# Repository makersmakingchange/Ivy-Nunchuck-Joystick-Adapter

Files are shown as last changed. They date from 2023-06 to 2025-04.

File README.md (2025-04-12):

 # Ivy Nunchuck Joystick Adapter

The Ivy Nunchuck Adapter allows a Nunchuck Controller to be used as a USB HID Mouse or USB HID Gamepad. 

Commercially available Nunchuck Controllers have a thumbstick and two buttons. The thumbstick has a range of motion approximately ±30° (~±15 mm motion) and requires about 100 grams-force to fully deflect.

The device is comprised of off-the-shelf electronics that are assembled without the need to solder into a 3D printed enclosure. The overall cost of materials for the adapter is $20 (plus $8 for component shipping). Paired with an old Nintendo Wii Nunchuck controller or a Nunchuck Controller replacement ($10-$20), this provides a cost effective solution for an input device.

The Ivy Nunchuck Adapter can be used directly as a left or right thumbstick for the Microsoft Xbox Adaptive Controller (XAC) using the left or right USB ports.

The Ivy Nunchuck Adapter is open assistive technology (OpenAT). Under the terms of the open source licenses, the device may be built, used, and improved upon by anyone.

The current version of the Ivy Nunchuck Adapter (v1.0) has been built and user tested. 

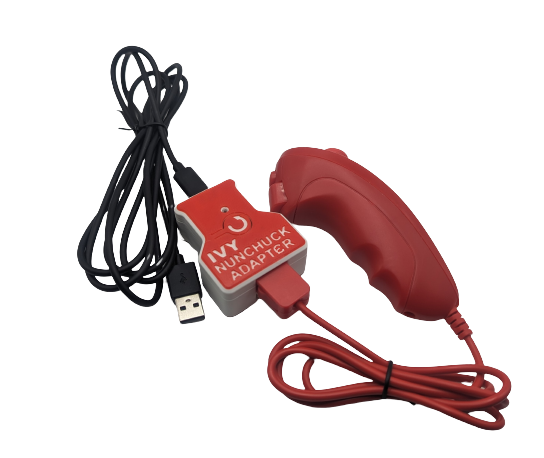
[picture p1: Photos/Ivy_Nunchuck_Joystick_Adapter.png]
An Ivy Nunchuck Adapter with a red Nunchuck controller.


MMC Assistive Device Library Listing: https://www.makersmakingchange.com/s/product/ivy-nunchuck-joystick-Adapter/01tJR0000009LBiYAM

## OpenAT Joysticks
This design is part of the [OpenAT Joystick project](https://github.com/makersmakingchange/OpenAT-Joysticks), a collection of open source designs for digital access and adapted gaming.  

## Usage
### Setup
1. Plug the Nunchuck Controller into the Ivy Nunchuck Adapter.
2. Plug the USB-C end of the USB Cable into the Ivy Nunchuck Adapter.
3. Connected the other end of the USB cable to the host device (use a suitable adapter if necessary).

### Swapping between Mouse and Gamepad Mode
1.	Reset the Adapter by pressing the Reset Button or removing and replacing the USB-C Cable.
2.	When the Status Light turns red, press and hold both the C Button and the Z Button on the Nunchuck.
3.	When the Status Light turns green, release the buttons. 
4.	Press the C button (round button) to toggle between modes. The light on the Adapter will indicate the current mode: USB HID Mouse - Yellow, USB HID Gamepad - Blue. 
5.	Press and release the Z button (square button) to set the mode. The light will blink in the colour of the selected mode.
6.	Reset the Adapter by pressing the Reset Button or removing and replacing the USB-C Cable.

### Mouse Mode
1. Move the joystick to control the cursor.
2. Press the C button to left click.
3. Press the Z button to right click.

### Gamepad Mode
1. Move the joystick to control the joystick.
2. Press the C button to activate Button 1.
3. Press the Z button to activate Button 2.

## How to Obtain a Ivy Nunchuck Adapter
There are several options for obtaining the device.

### 1. Do-it-Yourself (DIY) or Do-it-Together (DIT)

This is an open-source assistive technology, so anyone is free to build it. All of the files and instructions required to build the Ivy Nunchuck Adapter are contained within this repository. Refer to the Maker Guide below.

### 2. Request a build of this device

If you would like to obtain a Ivy Nunchuck Adapter, you may submit a build request through the [MMC Assistive Device Library Listing:](https://www.makersmakingchange.com/s/product/ivy-nunchuck-joystick-Adapter/01tJR0000009LBiYAM) to have a volunteer maker build the device. As the requestor, you are responsible for reimbursing the maker for the cost of materials and any shipping.

### 3. Build this device for someone else

If you have the skills and equipment to build this device, and would like to donate your time to create the switch for someone who needs it, visit the [MMC Maker Wanted](https://makersmakingchange.com/maker-wanted/) section.

## Build Instructions

### 1. Read through the Maker Guide
The [Maker Guide](/Documentation/Ivy_Nunchuck_Adapter_Maker_Guide.pdf) provides an overview of how to build, program, and test the device.

### 2. Use Maker Checklist
Work through the Maker Checklist. Confirm details and customization options with the user.

### 3. Order the Off-The-Shelf Components
The Bill of Materials([.csv](/Documentation/Ivy_Nunchuck_Joystick_Adapter_BOM.csv))([.xls](/Documentation/Working_Documents/Ivy_Nunchuck_Joystick_Adapter_BOM.xlsx)) lists all of the parts and components required to build the device.

### 4. Print the 3D Printable Components
Print the components for the enclosure. The print files can be found in the [/Build_Files/3D_Printing_Files](/Build_Files/3D_Printing/) folder. Reference the 3D Printing Guide section in the [Maker Guide](/Documentation/Ivy_Nunchuck_Adapter_Maker_Guide.pdf).

### 5. Assemble the Ivy Nunchuck Adapter.
Reference the Assembly Guide section of the [Maker Guide](/Documentation/Ivy_Nunchuck_Adapter_Maker_Guide.pdf) for the tools and steps required to assemble the device.

### 6. Flash the Ivy Nunchuck Adapter Firmware.
Reference the [Maker Guide](/Documentation/Ivy_Nunchuck_Adapter_Maker_Guide.pdf) for step-by-step instructions. The firmware is located in the [/Build_Files/Firmware_Files](/Build_Files/Firmware_Files/) folder.

## Files
### Documentation
| Document             | Version  | Link |
|----------------------|----------|------|
| Design Rationale     | 1.0      | [Ivy_Nunchuck_Joystick_Adapter_Design_Rationale](/Documentation/Ivy_Nunchuck_Joystick_Adapter_Design_Rationale.pdf)  |
| Maker Guide          | 1.1      | [Ivy_Nunchuck_Joystick_Adapter_Maker_Guide](/Documentation/Ivy_Nunchuck_Joystick_Adapter_Maker_Guide.pdf)          |
| Bill of Materials    | 1.0      | [Ivy_Nunchuck_Joystick_Adapter_Bill_of_Materials](/Documentation/Ivy_Nunchuck_Joystick-Adapter_BOM.csv)            |
| User Guide           | 1.0      | [Ivy_Nunchuck_Joystick_Adapter_User_Guide](/Documentation/Ivy_Nunchuck_Joystick_Adapter_User_Guide.pdf)              |

### Design Files
 - [CAD_Files](/Design_Files/CAD_Files)

### Build Files
 - [3D_Printing_Files](/Build_Files/3D_Printing_Files)
 - [Firmware_Files](/Build_Files/Firmware_Files/)

## License
Copyright (c) 2023-2025 Neil Squire / Makers Making Change.

This repository describes Open Hardware:
 - Everything needed or used to design, make, test, or prepare the Ivy Nunchuck Joystick Adapter is licensed under the [CERN 2.0 Weakly Reciprocal license (CERN-OHL-W v2) or later](https://cern.ch/cern-ohl ) .
 - All software is under the [GNU General Public License v3.0 (GPL-3.0)](https://www.gnu.org/licenses/gpl.html).
 - Accompanying material such as instruction manuals, videos, and other copyrightable works that are useful but not necessary to design, make, test, or prepare the Ivy Nunchuck Joystick Adapter are published under a [Creative Commons Attribution-ShareAlike 4.0 license (CC BY-SA 4.0)](https://creativecommons.org/licenses/by-sa/4.0/) .

You may redistribute and modify this documentation and make products using it under the terms of the [CERN-OHL-W v2](https://cern.ch/cern-ohl).
This documentation is distributed WITHOUT ANY EXPRESS OR IMPLIED WARRANTY, INCLUDING OF MERCHANTABILITY, SATISFACTORY QUALITY AND FITNESS FOR A PARTICULAR PURPOSE.
Please see the CERN-OHL-W v2 for applicable conditions.

Source Location: https://github.com/makersmakingchange/Ivy-Nunchuk-Joystick-Adapter

## Attribution
Several previous projects have interfaced with a Nunchuck controller to use it as a mouse or joystick including [USB Nunchuck Mouse](https://hackaday.io/project/188294-usbnunchuckmouse).

The [Adafruit QT Py](http://www.adafruit.com/products/4600) development board was designed by Limor Fried/Ladyada from Adafruit. The PCB design is [available open source](https://github.com/adafruit/Adafruit-QT-Py-PCB) under a CC-BY-SA license.

The [Adafruit Wii Nunchuck Breakout Adapter - Qwiic / STEMMA QT](https://www.adafruit.com/product/4836) board was designed by Limor Fried/Ladyada from Adafruit. The PCB design is [available open source](https://github.com/adafruit/Adafruit-Wii-Nunchuck-Breakout-Adapter-PCB)  under a CC-BY-SA license.

- The code utilizes the [WiiChuck](https://github.com/madhephaestus/WiiChuck) library by [Kevin Harrington (madhephaestus)](https://github.com/madhephaestus)) available under a [LGPL-3.0 license](https://www.gnu.org/licenses/lgpl-3.0.html).
 - The code also utilizes the [FlashStorage](https://github.com/cmaglie/FlashStorage) library by [Cristian Maglie (cmaglie)](https://github.com/cmaglie) available under a 
 [LGPL-2.1 license](https://www.gnu.org/licenses/lgpl-2.1.html).

 ### Contributors
- Jake McIvor, Neil Squire Society. Enclosure design, documentation, coding, testing,
- Milad Ha, Neil Squire Society. Coding.
- Josie Versloot, Neil Squire Society. Coding, testing.
- Stephen Moyer, Neil Squire Society. Testing.
- Tyler Fentie, Neil Squire Society. Testing.

---

<!-- ABOUT MMC START -->
## About Makers Making Change
[Makers Making Change Logo](https://www.makersmakingchange.com/)

Makers Making Change is a program of [Neil Squire](https://www.neilsquire.ca/), a Canadian non-profit that uses technology, knowledge, and passion to empower people with disabilities.

Makers Making Change leverages the capacity of community based Makers, Disability Professionals and Volunteers to develop and deliver affordable Open Source Assistive Technologies.

 - Website: [www.MakersMakingChange.com](https://www.makersmakingchange.com/)
 - GitHub: [makersmakingchange](https://github.com/makersmakingchange)
 - Bluesky: [@makersmakingchange.bsky.social](https://bsky.app/profile/makersmakingchange.bsky.social)
 - Instagram: [@makersmakingchange](https://www.instagram.com/makersmakingchange)
 - Facebook: [makersmakechange](https://www.facebook.com/makersmakechange)
 - LinkedIn: [Neil Squire Society](https://www.linkedin.com/company/neil-squire-society/)
 - Thingiverse: [makersmakingchange](https://www.thingiverse.com/makersmakingchange/about)
 - Printables: [MakersMakingChange](https://www.printables.com/@MakersMakingChange)

### Contact Us
For technical questions, to get involved, or to share your experience we encourage you to [visit our website](https://www.makersmakingchange.com/) or [contact us](https://www.makersmakingchange.com/s/contact).
<!-- ABOUT MMC END -->

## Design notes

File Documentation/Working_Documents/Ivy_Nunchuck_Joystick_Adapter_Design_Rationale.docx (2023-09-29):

# Introduction

The Ivy Joystick is intended to be a wearable / graspable device for those with limited gross motor control and limited hand dexterity. This design is intended to add as additional cost-effective option for people with disabilities for adapted gaming or computer access.

# Requirements

## Who

Who will be using the device?

- The device is intended for use by people with disabilities that affect their ability to use traditional input devices like computer mice and video gaming controllers, especially those with limited gross motor control and limited hand dexterity.

Who will be affected by the device?

- The primary user.

## What

What must the device do?

- Act as a USB HID Mouse and/or USB HID Gamepad.
- The device is NOT intended to be used to control a mobility device.

What needs must the device serve?

- Users with limited dexterity
- Users with the following possible points of access:
  - Hand

## Why

Why will the device be used?

- Enable / improve ability for Digital Access (e.g., control mouse function on computer)
- Enable / improve ability for Adapted Gaming (e.g., control thumbstick on Xbox Adaptive Controller)

## Where

Where will the device be used?

- In a home.
  - At a desk
  - At a wheelchair
  - On a bed
  - On a couch
- In a physical rehab setting.

## When

When will the device be used?

- When using a computer or other compatible host device (e.g., gaming console).
- When testing out different gaming set-ups.

## Goals

G01 | Achieve a material cost of less than $80 CAD.
G02 | Maker manufacturable in quantities of one.
G03 | The use of support material in 3d printed components should be minimized.
G04 | The number of different filament types should be minimized.

## Functional Requirements

| Device must be operable in USB HID Mouse operating mode
| Device must be operable in USB HID Gamepad operating mode
| Device must be compatible with the Xbox Adaptive Controller.
| Primary User should be able to switch operating mode.
| Secondary User must be able to switch operating mode
| The housing shall protect internal components from outside sources.

## Non-functional Requirement

NF01 | Device is releasable with open source license
NF02 | Device must be maker manufacturable.
NF03 | Documentation should be maintainable with the use of commonly available software.
NF04 | Documentation must be available in a digital format.
NF05 | Documentation should be printable.

## Constraints

C01 | Not for use with mobility devices.
C02 | 3D printed components shall be printable within a 180x180x180mm print volume.
C03 | 3D printed components should be printable on consumer-grade FFF printer

# Research

## Existing Commercial Options

### Wii Nunchuck

https://en.wikipedia.org/wiki/Wii

https://en.wikipedia.org/wiki/Wii_Remote

Wii Nunchuck (RVL-004)

- Analog stick
- Octagonal movement restriction
- Two trigger buttons
- Three-axis accelerometer
- 113 mm long x 38 mm wide x 37 mm thick

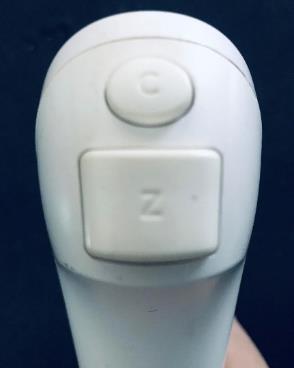
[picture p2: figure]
Nintendo Wii Nunchuk front view

Figure 1 Nintendo Wii Nunchuck. Born2BGod, CC BY-SA 4.0 <https://creativecommons.org/licenses/by-sa/4.0>, via Wikimedia Commons

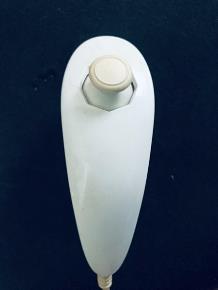
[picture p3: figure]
Nintendo Wii Nunchuk top view

Figure 2. Wii Nunchuck top. Born2BGod, CC BY-SA 4.0 <https://creativecommons.org/licenses/by-sa/4.0>, via Wikimedia Commons

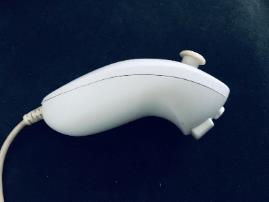
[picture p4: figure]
Nintendo Wii Nunchuk side view

Figure 3. Wii Nunchuck Side. Born2BGod, CC BY-SA 4.0 <https://creativecommons.org/licenses/by-sa/4.0>, via Wikimedia Commons. https://commons.wikimedia.org/wiki/File:Nunchuck_Side.jpg.

The Nintendo Wii Nunchuk controller has a proprietary connector, and by default is only able to connect to the Nintendo Wii via a Nintendo Wiimote.

### PDP One-Handed Controller

Title | PDP One-Handed Controller
Link | https://www.microsoft.com/en-ca/d/pdp-one-handed-joystick-for-xbox-adaptive-controller/8qhw8mlwpp1l
Cost | Discontinued
Notes | This is one of the only joystick accessories listed with the Xbox Adaptive Controller. Unfortunately it is no longer available.

### Wii® Nunchuck Joystick Adapter MK2 For XBOX® Adaptive Controller

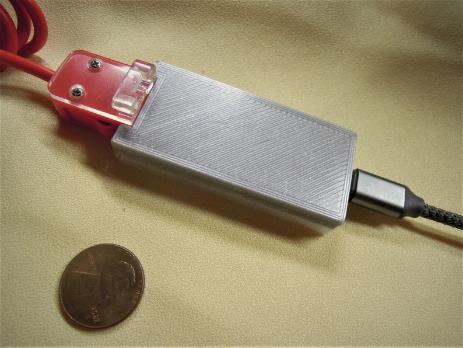
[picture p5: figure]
Wii® Nunchuck Joystick Adapter MK2 For XBOX® Adaptive image 6

Title | Wii® Nunchuck Joystick Adapter MK2 For XBOX® Adaptive Controller
Link | https://www.etsy.com/ca/listing/1245123261/wii-nunchuck-joystick-adapter-mk2-for
Cost | $50-70 CAD
Notes | An adapter for connecting a Wii Nunchuck / Nunchuck controller to the Xbox Adaptive Controller.

## DIY Designs

### USB Mouse Made Out of a Wii Nunchuck

Title | USB Mouse Made Out of a Wii Nunchuck
Link | https://www.instructables.com/USB-Mouse-Made-Out-Of-A-Wii-Nunchuck/
Author
License | CC BY-NC-SA
Cost
Notes | This build requires permanent modification of the Nunchuck. The built-in board on the Nunchuck is disconnected and removed and the buttons and joystick are connected to a Teensy microcontroller.

### Nunchuck Mouse

Title | Nunchuck Mouse
Link | https://www.instructables.com/nunchuck-mouse/
Author | Krayzi99
License | CC BY-NC-SA
Cost
Notes | This build uses a Nunchuck with a Bluetooth adapter and software that translates the information into mouse commands.

### USB Wiichuck Mouse Using an Arduino Leonardo

Title | USB Wiichuck Mouse Using an Arduino Leonardo
Link | https://www.instructables.com/USB-Wiichuck-Mouse-Using-an-Arduino-Leonardo/
Author
License | CC BY-NC-SA
Cost
Notes

### Programmable ambidextrous joystick mouse

Title | Programmable ambidextrous joystick mouse
Link | https://hackaday.io/project/174547-programmable-ambidextrous-joystick-mouse
Author | NDB
License | n/a
Cost | n/a
Notes | Early conceptual design.

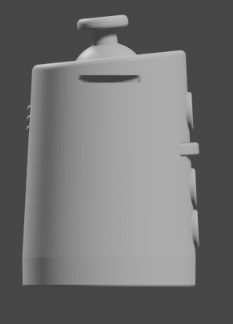
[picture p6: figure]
CAD Screenshot of Programmable ambidextrous joystick mouse. Has a single thumstick on top and three buttons on the side.

Figure 4. CAD Screenshot of Programmable ambidextrous joystick mouse.

- 3 buttons
- Vibration feedback
- Configuration application

### Joytojoy

Title | Joytojoy
Link | https://hackaday.io/project/186678
Author | Julien Oudin
License
Cost
Notes | Gyro-based joystick intended to mount on top of a user’s powerchair joystick.

### One Handed Keymouse

Title | One Handed Keymouse
Link | https://hackaday.io/project/7254-one-handed-keymouse
Author | Patrick Tait
License | Software: BSD; CC-BY
Cost
Notes

### 3D Printed Joystick

Title | 3D Printed Joystick
Link | https://hackaday.io/project/172309-3d-printed-joystick
Author
License
Cost
Notes | Uses an LED, fiber optic cables, and a camera to measure different amounts of light that are transmitted in response to 3d printed joystick components.

### Eyemech Controller

Title | Eyemech Controller
Link | http://www.nilheim.co.uk/latest-projects-and-blog/eyemech-controller
Author | Will Cogley
License | Unknown
Cost
Notes | 3D printable, handheld device

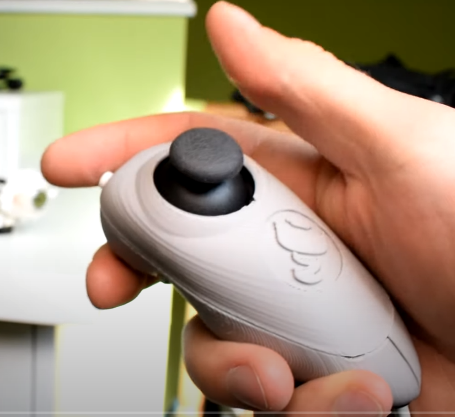
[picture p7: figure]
Eyemech controller being held in a hand.

Figure 5 Eyemech Controller. (C) Will Cogley.

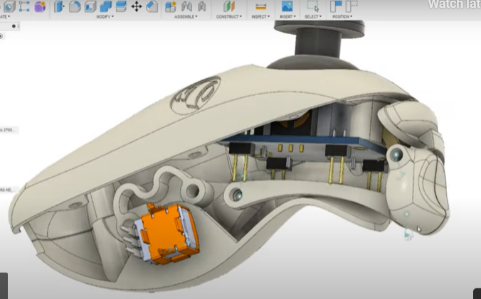
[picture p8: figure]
CAD screenshot of Eyemech controller showing internal components

Figure 6. Eyemech controller CAD Model. (C) Will Cogley

### USB Nunchuck Mouse

Title | USB Nunchuck Mouse
Link | https://hackaday.io/project/188294-usbnunchuckmouse
Author | Esp32beans
License | Unknown
Cost | Nunchuck: $12.50 USD; Breakout: $2.50 USD; $12.50 USD
Test Build (Y/N) | Y
Add to Library (Y/N) | TBD
Notes | Uses nunchuck clone and Adafruit interface board (https://www.adafruit.com/product/4836).

## Research Summary

There are limited commercially available options that are capable of mouse control. There are a wide variety of DIY designs for handheld controllers that can be the basis for a design that has the ability to act both as a gamepad and a mouse, a feature that seems missing.

# Ideation

## Architecture

The inspiration for the name ‘Ivy’ came from the concept of using a reusable rubber twist tie / gear tie to connect to the handheld controller and wrap around the arm.

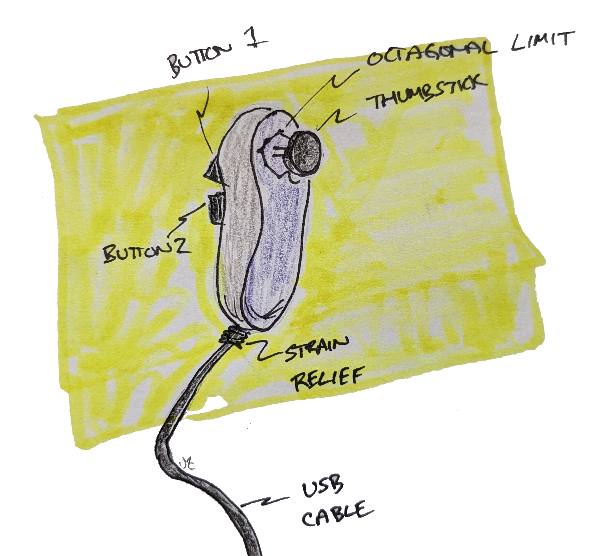
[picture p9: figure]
Concept sketch of handheld controller with main features: thumstick, octagonal limiter, button 1, button 2, strain relief, and USB cable.

Figure 7. Handheld Controller Concept Sketch

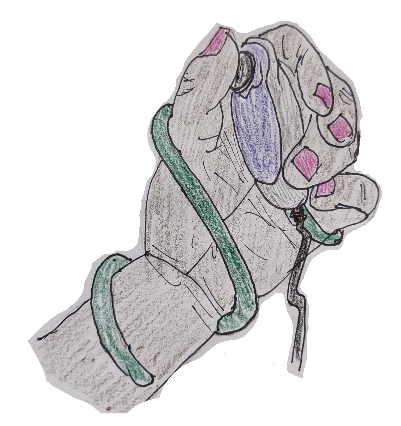
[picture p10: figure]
Concept sketch of a controller in a users hand with a green twist tie keeping it in place.

Figure 8. ‘Wearable’ Ivy Concept with Green Twist Tie

## Key Functions

1. Mode switching - Need a way to operate and switch between mouse mode and joystick mode, since compatibility with the XAC currently requires that the device only appears as a USB Gamepad.
2. Inputs
  a. Cursor/Joystick control + 2-3 inputs

## Commercially Available Joystick Modules

What type of joystick element makes the most sense?

Commercial joystick elements

- PS2 Thumbstick
- Sliding thumbstick
- Nintendo Joycon style thumbstick
- Custom Joystick Element

## Design Elements

- Removable handle
- Finger grooves / Grip
- How to accommodate different sized hands
  - Two part
  - Instamorph?
  - Shrink wrap?
  - Bike wrap?
  - Dycem
  - Uva foam
  - Foam sheets
- How to affix sheets?
  - Clamps
  - Glue

## Assembly

- Two piece clam shell
- Three piece
  - Right
  - Left
  - Top
  - Screws + a couple locating pins

Affixing joystick into enclosure

- Conical print
- Screws
- Snap-fit

## Tactile Feedback

Could a tactile feedback element be added here?

e.g., i2C Haptic Driver controller + Haptic motor.

## Button Options

- Integrated buttons
- Integrated switch jacks

## Mounting

- Flexible twist tie wrap mounting – e.g., wrapping around arm like ivy
- Modular – integration with cuff style
- Interface with Instamorph for custom fit

### Modular Mounting Connection

- separate handle portion
  - allows for customized sizes / colours / etc
  - more printable
- dove tail connection between main body and handle

# Conceptual Design

## Concepts

1. Utilizing commercially available Nunchuck controller from Nintendo or a knock-off.
2. Novel 3D printed Nunchuck-style controller

Nunchuck controllers and knockoffs are readily available via Amazon and electronics suppliers, are fairly cost effective ($12-15 CAD ea.), and may also be available at little to no cost used. The controller features a thumbstick, two buttons, and an embedded accelerometer.

## Nunchuck Controller Concept

Summary: Utilize an existing Nintendo Nunchuck or equivalent in addition to Adafruit Breakout board + Microcontroller.

### Architecture

1. Utilize Nunchuck (or knock-off) as-is, mount interface electronics in stand-alone box.
2. Open Nunchuck (or knock-off) and embed interface electronics within existing enclosure.
3. Extract electronics from Nunchuck (or knock-off) and incorporate into custom enclosure.

#### Stand-alone Box

This is the simplest approach. It does not require any modification to the existing controller. Basic assembly can also be completed without the use of soldering by utilizing a STEMMA QT cable with the Nunchuck Breakout board and a development board cwith a STEMMA QT connection (e.g., Adafruit SAMD21 QtPy).

#### Embedded Electronics

This approach requires the Nunchuck to be disassembled, permanently modified, and then reassembled.

Disassembling the Nunchuck requires a small Phillips screwdriver (i.e., No. 0) to remove the two small screws holding the two parts of the enclosure together. The existing cable assembly consists of 5 wires and a molded in strain relief. The wires would need to be cut and soldered either directly to the microcontroller development board or to the pads on the Nunchuck breakout board. The is some available space within the enclosure, but not quite enough to accommodate the QtPy board with a standard USB-C cable to use the existing cable hole. It looks like some of the inner support ribs could be cut to provide sufficient space for the dev board and cable.

The other option here would be to remove the existing i2C circuitry and connect the joystick and buttons directly to the microcontroller. It also unclear how much variation may exist between Nunchuck controllers from different manufacturers.

#### Incorporated components

This approach involves disassembling a Nunchuck controller, removing the electronics components and incorporating them into a different enclosure.

It’s not known how consistent the internals are between models of the Nunchuck from different suppliers.

### Nunchuck Mounting

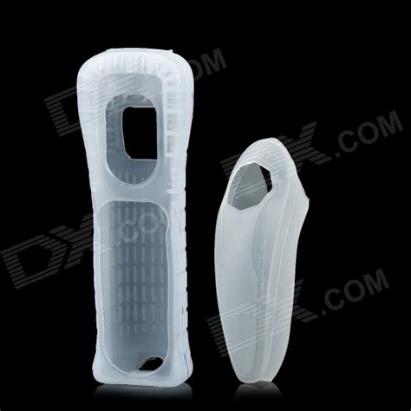
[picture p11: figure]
Commercially available silicone sleeves for Wiimote and Nunchuk

Figure 9. Commercially available controller sleeves.

Mounting Ideation

- Commercially available silicon sleeve
- 3D Printed Add-on?
- Interface with mounting screw
- Instamorph?

### Circuitry

The Nunchuck controller uses an i2C interface with a proprietary connector. Interfacing with the circuitry could happen within the Nunchuck enclosure, by cutting the cable, or by using a suitable adapter with the connector.

### Code

There is an existing open source library, the WiiChuck Library, for interfacing with the controller.

https://github.com/madhephaestus/WiiChuck

LGPL-3.0 License

## Novel 3D Printed Enclosure Concept

Summary: Create a novel enclosure with electronic elements like the Nunchuck controller.

### Components

#### Amazon Joycon Replacement Joystick

Jeylly Original 3D Analog Joystick Joy-Con Replacement Left/Right Repair Kit Thumb Sticks Sensor with 4 “Y” Screws for Nintendo Switch Joycon Controller and Switch Lite Console - 2 Pack White https://www.amazon.ca/dp/B08B4K4NCV - $11.23

- This is intended as a replacement for the thumbstick in the Joycon controller. It is not the same part as the Adafruit PSP 3000 2-Axis Analog Thumb Joystick (https://www.adafruit.com/product/3103)
- The cable is intended to be used with a Zero Force Insertion (ZIF) connector it a 5P 0.5 mm pitch connector.
- The connector does not fit the Adafruit Touch screen breakout board (0.5mm FPC) (https://www.adafruit.com/product/334)
- The connector does not fit the other 0,5mm FPC connector from Amazon.
- It has two two ~1.6 mm holes; M1.7 screws were too big; M1.4 screws fit okay; the joycon is connected to the joycon controller with two 3.5 mm Phillips #00 screws[^1].
- Surface mount connector: https://www.mouser.ca/ProductDetail/Amphenol-FCI/59453-051110ECHLF?qs=SqJKR5Mmryc5fGwXZgOgcA%3D%3D
- It doesn’t appear as though any 0.5 mm pitch, 5 position connectors are available in thru hole format or as a breakout board.

### Electrical Connections

#### Protoboard

Universal Proto-board PCBs 4cm x 6cm - 3 Pack

- https://www.adafruit.com/product/4785
- 3 pack
- 4 cm x 6 cm

Universal Proto-board PCBs 3cm x 7cm

- 3-pack: https://www.adafruit.com/product/4784
- 3 cm x 7 cm
- Can score with hobby knife and ruler and break to size

#### 3D Printed Circuit Board

Flexible Protoboard

https://www.adafruit.com/product/3904e.g. https://www.adafruit.com/product/3904

20cm x 30 cm

Adafruit Flex Perma-Proto - Half-sized Breadboard Flex-PCB

- https://www.adafruit.com/product/1518
- 79 mm x 43 mm

## Mode Switching

1. Hardware-based mode switching (e.g., an additional button or switch on the device)
2. Software-based mode switching

## Concept Selection

The Nunchuck Concept with the Stand-alone box architecture was selected for development for the MVP. It provides a simple, solderless way to create a controller, the parts are readily available, and components are cost-effective. The biggest limitation is that standard Nunchuck controllers only have two buttons.

# Detailed Design

## Electronics

### Electronic Components

This approach requires an Adafruit Wii Nunchuck Breakout board and an i2C-compatible microcontroller. The Adafruit QTPY SAMD21 was selected as it is cost effective, readily available, has an interchangeable footprint with other microcontrollers and has a built-in STEMMA QT connector.

### Circuitry

This circuitry is simple; the Nunchuck Breakout board must be attached to the microcontroller via a STEMMA QT cable.

## Enclosure

The enclosure must securely hold the microcontroller and the Nunchuck breakout board.

### Nunchuck Controller Clearance / Knockout

The enclosure must have adequate clearance to allow the Nunchuck controller to be attached. See measured dimensions below.

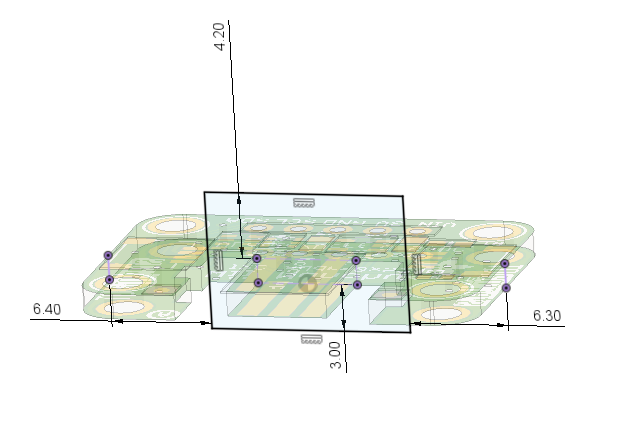
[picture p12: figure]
CAD screenshot of Nunchuck connector breakout dimensions.
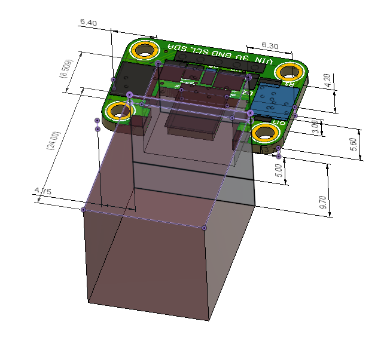
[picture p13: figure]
CAD screenshot of Nunchuck connector breakout volume.

Figure 10. Nunchuck Connector Breakout Dimensions

### Component Arrangement

Two arrangements were considered: an inline arrangement with Nunchuck connection on one side and USB connection on the other side, and a single sided arrangement with both connections on the same side. The in-line arrangement was selected in attempt to better manage cables and provide a logical flow as an ‘Adapter’.

### Electronic Component Mounting

To reduce the number of components, cost, and build complexity, the electronics were attached into the enclosure without the use of fasteners. The Adafruit QTPY board was secured with snap fit elements and the Nunchuck breakout board was secured using posts through the mounting holes. Ideally only one method would be used, but QTPY board does not have mounting holes and there was insufficient room on the edges of the breakout board to allow for snap-fits.

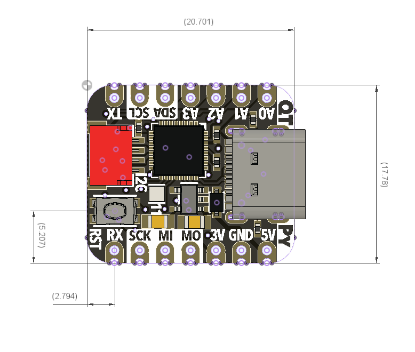
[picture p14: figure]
CAD screenshot of Adafruit QT Py Development board showing overall dimensions and location of reset button

Figure 11. Adafruit QT Py Development Board Dimension.

### Enclosure Architecture

Again, to minimize the number of tools and components required, the enclosure was designed to use snap fits to attach the top part of the enclosure to the bottom part of the enclosure. A two-piece enclosure provides for easy assembly.

### Enclosure Features

The enclosure features a print-in-place flexible element for pressing the reset button on the microcontroller. It also features a hole for a light pipe so the LED on the microcontroller can be viewed from the outside of the enclosure.

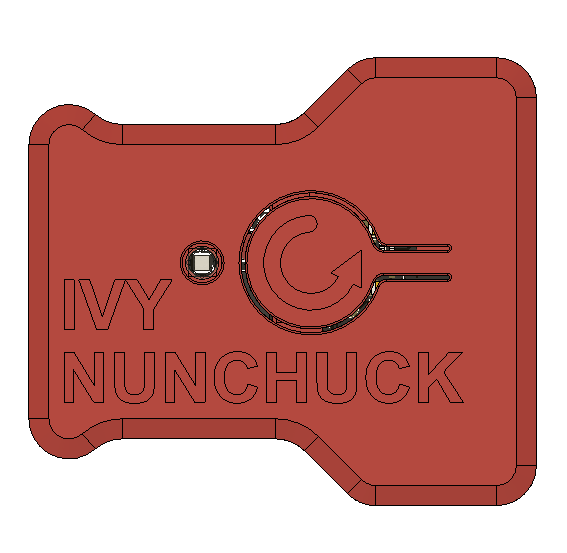
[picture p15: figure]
Top view of V0.1 enclosure

Figure 12 V0.1 Enclosure Top View

#### Reset Button

The reset button is modelled after a typical reset button on a computer with a circular arrow shape.

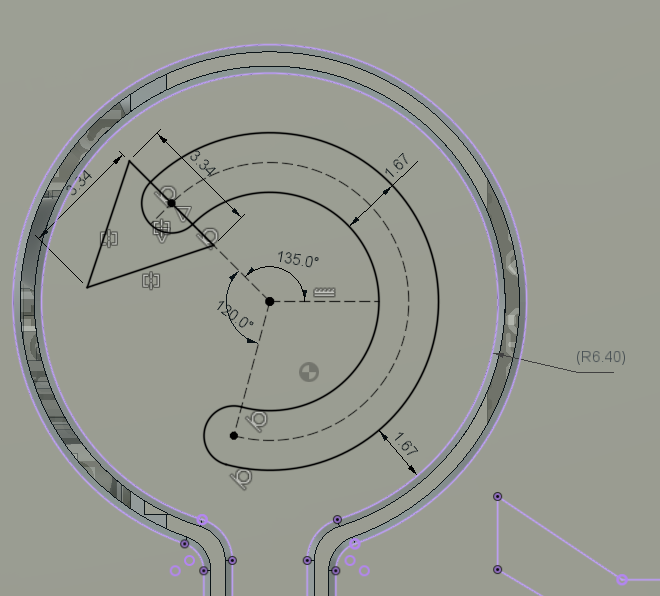
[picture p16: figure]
CAD screenshot of dimensioned reset label

Figure 13. Reset Label

#### Enclosure Snap-Fit

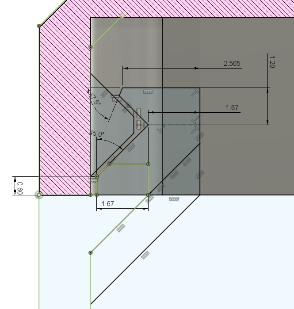
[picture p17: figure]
CAD screenshot of enclosure snap-fit dimensions

Figure 14. Enclosure Snap-fit dimensions.

#### Light Pipe

A light pipe was added to help increase the visibility of the LED light on the development board. The model was selected based on what has currently been used in other MMC projects.

Light Pipe

- Counterbore Diameter: 4 mm
- Counterbore Depth: 0.8 mm
- Press fit diameter: 2.8 mm

#### Overall Enclosure

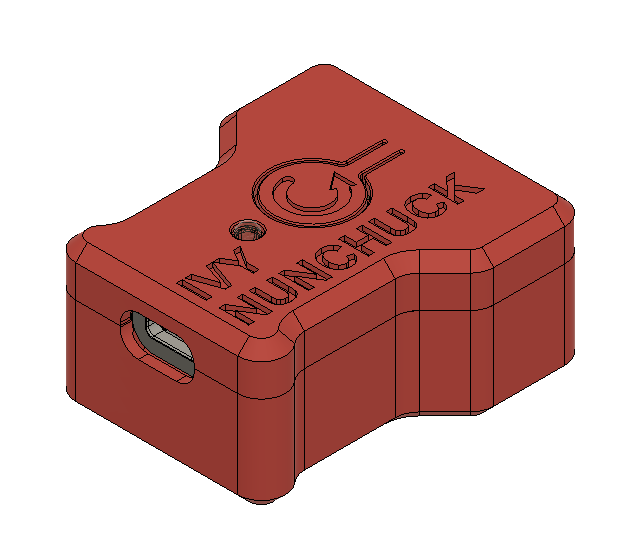
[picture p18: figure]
Isometric CAD screenshot of v0.1 enclosure

Figure 15. Isometric view of enclosure showing USB connection side.

## Software

The software was based on previous work developed for the OpenAT Joysticks. That software was modified to utilize the WiiChuck library for managing communication to the Nunchuck Controller.

Some progress was made towards an integrated object-oriented approach to managing different types of joystick sensors. A JoystickInput class was created with derived classes for different types of Joystick Input devices like potentiometers, Hall effect, and the Nunchuck.

## Naming

NUN-CHUCK and NUNCHUK are still registered trademarks in Canada owned by Nintendo. NUNCHUCK seems to be a commonly used term for the controllers and the breakout board. For that reason, Nunchuck seems like the better choice.

Adaptor vs Adapter are both used commonly and often interchangeably. Adaptor was initially chosen based on being more traditional, and referring to a device rather than a person, however Adapter is the more commonly used term in North America and would be a better choice.

# Ivy Nunchuck Joystick Adapter V0.1

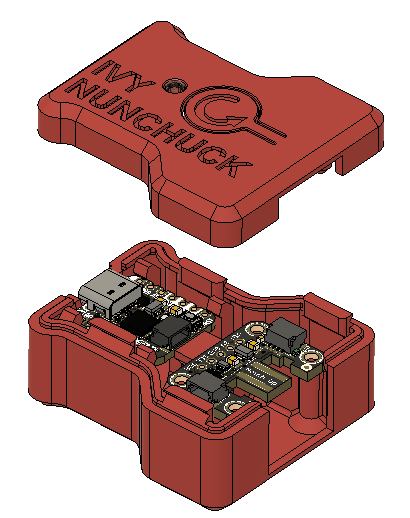
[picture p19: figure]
CAD screenshot of exploded view of v0.1 Ivy Nunchuck.

Figure 16. Exploded View (v0.1)

## Testing

### Research Questions

- Ability to switch between mouse and joystick
  - Different code / code flags
  - Add slide switch?
- Third button for mouse / scroll?
  - Accelerometer / gryo
  - Activated with both buttons
    - Toggle
  - Add switch jack to box
- Mounting?
- Do we need the USB cover component? Can this be made more printable?
- Need / alternatives for light pipe?

## Feedback

The USB-C cover component is quite small, and therefore challenging to print. It didn’t provide much benefit over an integrated cover portion.

Activating scroll mode via long-button press is annoying for flipping back and forth.

The timing of pressing the two buttons after a reset to enter the mode switching can be difficult.

Cycling between desired modes during mode switching is difficult (inadequate delay / switch debounce)

# Ivy Nunchuck Joystick Adapter V1.0

## Features

1. Simple assembly – no soldering or tools required.
2. Print-in-place reset button pusher

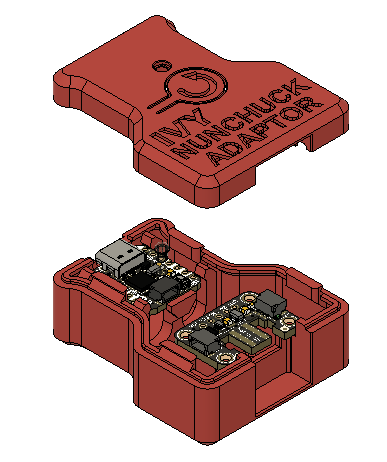
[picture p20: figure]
CAD screenshot of opened Ivy Nunchuck Adaptor showing internal electronic components.

Figure 17. Exploded View (v1.0)

## Design Changes

1. The length of the enclosure was increased to increase the spacing and clearance for the STEMMA QT Cable.
2. The enclosure snap fit elements near the dev board were shifted so they didn’t interfere with the dev board snap fits.
3. Additional material was added near the Nunchuck breakout board to better enclose the Nunchuck connector.
4. The CAD model was cleaned up to remove earlier design elements that were no longer required (e.g., bosses for headers).

## Opportunities for Improvement / Future Work

1. Investigate methods to improve scroll functionality
  a. E.g., Button 1 and Button 2 simultaneously, Button sequence
2. Add additional control Modes (e.g. accelerometer based cursor control)
  a. IMU for cursor control; joystick for scroll (or buttons?)
3. Second joystick via i2c Seesaw?
4. Investigate additional mounting options
5. Consider capturing either USB cable, Nunchuck controller, or both
6. Research existing topper designs and/or develop toppers designs for Nunchuck Controller thumbstick
7. Detail and test the different adapter options for connecting to different consoles / host devices.
  a. Mayflash to connect with Nintendo Switch
8. Add code to handle disconnected Nunchuck
9. Code / physical method to disable mouse output in case something goes wrong with code.
10. Investigate options for creating an analog version of the Nunchuck.
  a. e.g., Nunchuck controller, TRRS cable, 2X mono cables.
11. Implement time-based mouse acceleration
12. Implement input switch debouncing
13. Add option for adding strap or cuff to Nunchuck Controller

[^1] https://www.ifixit.com/Guide/Left+Joy-Con+Joystick+Replacement/113182

© 2023 by Neil Squire Society. This work is licensed under the CC BY SA 4.0 License: http://creativecommons.org/licenses/by-sa/4.0 Files available at https://github.com/makersmakingchange/Ivy-Nunchuk-Joystick-Adapter Page 1 of 1

V1.0 | SEPTEMBER 2023 Ivy Nunchuck Joystick Adapter Design Rationale

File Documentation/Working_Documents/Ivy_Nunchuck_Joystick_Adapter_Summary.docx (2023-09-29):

This document is intended to be a summary of a device to make it easier to add to the website.

# Product Information

## Product Name

Ivy Nunchuck Joystick Adapter

## Device Category

Adapted Toys

Aids for Daily Living (ADL)

Assistive Switches

Communication Aids (AAC)

Computer Access

Environmental Controls

Gaming

Keyguard

Kits

LipSyncs

Mounting

Recreation and Leisure

Seating and Positioning

Switch Interfaces

Writing Aids

## User Value Statement

## If you love the freedom of your old Wii Nunchuk style controller the Ivy Nunchuck Joystick Adapter is an easy to use package that lets you plug it in anywhere you need a USB mouse, or USB gaming joystick.

## Designer

Makers Making Change

# Device Info

## Overview

The Ivy Nunchuck Adapter allows a Nunchuck Controller to be used as a USB HID Mouse or USB HID Gamepad. The device is comprised of off-the-shelf electronics that are assembled without the need to solder into a 3D printed enclosure. The overall cost of materials for the adapter is $20 (plus $8 for component shipping). Paired with an old Nintendo Wii Nunchuk controller or a Nunchuck Controller replacement ($10-$20), this provides a cost-effective solution for an input device.

## Disability Type

Select one or more disability types:

Agility / Dexterity

Arthritis

Cognitive

Hearing

Mobility

Other

Pain

SCI

Vision

## Disability Type Description

For anyone who likes the function of the Wii style Nunchuck Controller and wants to expand it for use as either a USB mouse or USB gaming joystick.

## How To Use

For full instructions please refer to the User Guide (https://github.com/makersmakingchange/Ivy-Nunchuk-Joystick-Adaptor/blob/main/Documentation/Ivy-Nunchuck-Joystick-Adapter_User_Guide.pdf).

Usage

Using the Joystick

1. Plug the USB cable from the Ivy Adapter into the host device.
2. Hold or mount the Nunchuck controller as needed.
3. Move the Nunchuck joystick as you would with a standard controller.

Compatibility

- USB HID Mouse: PC, Mac, Android Smartphone, Apple Smartphone (iOS 13+)
- USB HID Gamepad: PC, Xbox Adaptive Controller, Android Smartphone, Apple Smartphone (iOS 13+)

The estimated material cost of the device:

$0 - $10

$11 - $25

$26 - $50

$51 - $100

$101 - $250

$250+

## Attribution

Several previous projects have interfaced with a Nunchuck controller to use it as a mouse or joystick including USB Nunchuck Mouse (https://hackaday.io/project/188294-usbnunchuckmouse).

The Adafruit QT Py (http://www.adafruit.com/products/4600) development board was designed by Limor Fried/Ladyada from Adafruit. The PCB design is available open source (https://github.com/adafruit/Adafruit-QT-Py-PCB) under a CC-BY-SA license.

The Adafruit Wii Nunchuck Breakout Adapter - Qwiic / STEMMA QT (https://www.adafruit.com/product/4836) board was designed by Limor Fried/Ladyada from Adafruit. The PCB design is available open source (https://github.com/adafruit/Adafruit-Wii-Nunchuck-Breakout-Adapter-PCB) under a CC-BY-SA license.

The firmware utilizes the WiiChuck (https://github.com/madhephaestus/WiiChuck) library by Kevin Harrington (madhephaestus) (https://github.com/madhephaestus)) available under a LGPL-3.0 license (https://www.gnu.org/licenses/lgpl-3.0.html).

The firmare also utilizes the FlashStorage (https://github.com/cmaglie/FlashStorage) library by Cristian Maglie (cmaglie) (https://github.com/cmaglie) available under a LGPL-2.1 license (https://www.gnu.org/licenses/lgpl-2.1.html).

# Maker Info

## Project Skills

3D Printing

Custom PCB

Electronics

Laser Cutting

Mechanics

Other

Software

Soldering

Woodworking

## Skills Description

This is an intermediate build requiring soldering and 3D printing.

## Tools Needed

3D Printer

Common Hand Tools

Common Power Tools

Laser Cutter

Soldering Iron

Specialized Tooling

## Print time (hrs)

2

## Assembly time (hrs)

0.25

## Build Instructions

This build consists of off-the-shelf electronics that are assembled into a 3D printed enclosure and flashed with firmware. For full details please refer to the Maker Guide (https://github.com/makersmakingchange/Ivy-Nunchuk-Joystick-Adaptor/blob/main/Documentation/Ivy_Nunchuck_Joystick_Adaptor_Maker_Guide.pdf).

Print Settings:

- 0.2mm Layer Height
- 20% infill
- Some optional parts require supports

## Download Link

https://github.com/makersmakingchange/Ivy-Nunchuk-Joystick-Adapter/archive/refs/heads/main.zip

## Project Link

https://github.com/makersmakingchange/Ivy-Nunchuk-Joystick-Adapter

# License

## License

Hardware: CERN 2.0 Weakly Reciprocal license

Software: GNU General Public License v3.0 (GPL-3.0)

Documentation: Attribution-ShareAlike4.0 International

© 2023 by Neil Squire Society. This work is licensed under the CC BY SA 4.0 License: http://creativecommons.org/licenses/by-sa/4.0 Files available at https://github.com/makersmakingchange/Iv-Nunchuck-Joystick-Adapter Page 1 of 2

V1.0 | September 2023 Ivy Nunchuck Joystick Adapter Summary

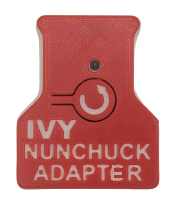
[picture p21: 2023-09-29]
Photos/Ivy_Nunchuck_Joystick_Adapter_Top.png

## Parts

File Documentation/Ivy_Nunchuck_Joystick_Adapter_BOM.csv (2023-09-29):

 | Ivy Nunchuck Joystick Adapter |  |  |  |  |  |  | Filament (g) |  | Unit Cost | Total Cost | Total Print time (hr)
 | Version: V1.0 | Last updated: | 2023-Sep-29 |  |  |  |  | 23 |  | $41.49 | $40.80 | 1:48
 | Commercial Parts |  |  |  |  |  |  |  | 1.35
ID | Part | Description | Manufacturer | Supplier | Supplier PN | QTY | QTY/PKG | PKGs | $/PKG | Unit Cost | Total Price |  | Link
8 | Wii Nunchuk Controller |  | Ostent | Amazon |  | 1 | 1 | 1 | $11.49 | $11.49 | $11.49 |  | https://www.amazon.ca/dp/B00FJ2LMGK
2 | Adafruit Wii Nunchuk Breakout |  | Adafruit | Digikey | 1528-4836-ND | 1 | 1 | 1 | $4.24 | $4.24 | $4.24 |  | https://www.digikey.ca/en/products/detail/adafruit-industries-llc/4836/13577615
3 | Qwiic Cable - 50 mm |  | Sparkfun Electronics | Digikey | 1568-1710-ND | 1 | 1 | 1 | $1.37 | $1.37 | $1.37 |  | https://www.digikey.ca/en/products/detail/sparkfun-electronics/PRT-14426/7652739
1 | Adafruit QT PY - SAMD21 |  | Adafruit | Digikey | 1528-4600-ND | 1 | 1 | 1 | 10.79 | $10.79 | $10.79 |  | https://www.digikey.ca/en/products/detail/adafruit-industries-llc/4600/13543375
4 | USB C Cable, 2m |  | Cvilux USA | Digikey | 2987-DH-20M50053-ND | 1 | 1 | 1 | $3.25 | $3.25 | $3.25 |  | https://www.digikey.ca/en/products/detail/cvilux-usa/DH-20M50053/13177348
5 | Light Pipe 0.250" |  | Dialight | Digikey | 350-3746-ND | 1 | 1 | 1 | $1.66 | $1.66 | $1.66 |  | https://www.digikey.ca/en/products/detail/dialight/51513030250F/4965201
 | Shipping |  |  | Digikey |  | 1 | 1 | 1 | $8.00 | $8.00 | $8.00
 | 3D Printed Parts | ESTIMATED PRICING USING 1KG ROLL COST: |  |  |  |  |  |  | $30.00
 | Part | Description |  |  |  | QTY | Mass (g) Per | TotalMass | $/gram |  | Total Price | Print Time (hr:Min) | Link
6 | Enclosure Top | Ivy_Enclosure_Top.stl |  |  |  | 1 | 8 | 8 | $0.03 | $0.24 | $0.24 | 0:36
7 | Enclosure Bottom | Ivy_Enclosure_Bottom.stl |  |  |  | 1 | 15 | 15 | $0.03 | $0.45 | $0.45 | 1:12
 | Alternatives (if there are other sources for some parts link them below)
 | Part | Description | Manufacturer | Supplier | Supplier PN | QTY | QTY/PKG | PKGs | $/PKG | Unit Cost | Total Price |  | Link
8 | Wii Nunchuk Controller |  | Adafruit | Adafruit | 342 | 1 | 1 | 1 | $16.88 | $16.88 | $16.88 |  | https://www.adafruit.com/product/342
2 | Adafruit Wii Nunchuk Breakout |  | Adafruit | Adafruit | 4836 | 1 | 1 | 1 | $3.98 | $3.98 | $3.98 |  | https://www.adafruit.com/product/4836
3 | Qwiic Cable - 50 mm |  | Adafruit | Adafruit | 4399 | 1 | 1 | 1 | $1.28 | $1.28 | $1.28 |  | https://www.adafruit.com/product/4399
1 | Adafruit QT PY - SAMD21 |  | Adafruit | Adafruit | 4600 | 1 | 1 | 1 | $10.13 | $10.13 | $10.13 |  | https://www.adafruit.com/product/4600
4 | USB C Cable, 3ft |  | Adafruit | Adafruit | 4474 | 1 | 1 | 1 | $6.28 | $6.28 | $6.28 |  | https://www.adafruit.com/product/4474
 | Adafruit Shipping |  |  | Adafruit |  | 1 | 1 | 1 | $27.00 | $27.00 | $27.00
 |  |  |  |  |  |  |  | 0 |  | $- | $-
8 | Wii Nunchuk Controller |  | Ostent | Mouser | 485-342 | 1 | 1 | 1 | $18.13 | $18.13 | $18.13 |  | https://www.mouser.ca/ProductDetail/Adafruit/342?qs=GURawfaeGuDV1HPrkucg9w%3D%3D
2 | Adafruit Wii Nunchuk Breakout |  | Adafruit | Mouser | 485-4836 | 1 | 1 | 1 | $4.28 | $4.28 | $4.28 |  | https://www.mouser.ca/ProductDetail/Adafruit/4836?qs=eP2BKZSCXI4ZoRtk7kHCZA%3D%3D
3 | Qwiic Cable - 50 mm |  | Sparkfun Electronics | Mouser | 485-4399 | 1 | 1 | 1 | $1.38 | $1.38 | $1.38 |  | https://www.mouser.ca/ProductDetail/SparkFun/PRT-14426?qs=wd5RIQLrsJiogglVGK6o1w%3D%3D
1 | Adafruit QT PY - SAMD21 |  | Adafruit | Mouser | 485-4600 | 1 | 1 | 1 | $10.88 | $10.88 | $10.88 |  | https://www.mouser.ca/ProductDetail/Adafruit/4600?qs=hd1VzrDQEGi752M4exorSA%3D%3D
4 | USB C Cable, 3ft |  | Adafruit | Mouser | 485-4474 | 0 | 1 | 0 | $7.18 | $- | $- |  | https://www.mouser.ca/ProductDetail/Adafruit/4474?qs=CUBnOrq4ZJz9F%2FNF%252BRRALQ%3D%3D
4 | USB C Cable, 2m |  | Adafruit | Mouser | 485-5044 | 1 | 1 | 1 | $5.73 | $5.73 | $5.73 |  | https://www.mouser.ca/ProductDetail/Adafruit/5044?qs=pBJMDPsKWf0NCabokbqBvw%3D%3D
5 | Light Pipe 0.250" |  | Dialight | Mouser | 645-515-1303-0250F | 1 | 1 | 1 | $1.35 | $1.35 | $1.35 |  | https://www.mouser.ca/ProductDetail/Dialight/515-1303-0250F?qs=rkevp0fsrts4dv75K85%2FWA%3D%3D
 | Mouser Shipping |  |  | Mouser |  | 1 | 1 | 1 | $20.00 | $20.00 | $20.00
 |  |  |  |  |  |  |  | 0 |  | $- | $-
8 | Wii Nunchuk Controller |  | Adafruit | Digikey | 1528-342-ND | 1 | 1 | 1 | $19.17 | $19.17 | $19.17 |  | https://www.digikey.ca/en/products/detail/adafruit-industries-llc/342/10669902
 | USB C Cable, 3ft |  | Adafruit | Digikey | 1528-4474-ND | 1 | 1 | 1 | $7.59 | $7.59 | $7.59 |  | https://www.digikey.ca/en/products/detail/adafruit-industries-llc/4474/11587355

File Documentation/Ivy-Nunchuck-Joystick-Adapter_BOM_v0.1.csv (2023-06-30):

Ivy Nunchuk Joystick Adapter |  |  |  | Total Cost | Total Print time (hr) | Total filament (g)
Version: V0.1 | Last updated: 2023-Jun-09 |  |  | $41.30 | 1:58 | 20
Commercial Parts:
Part type | Part Name | Manufacturer | Supplier | Quantity Needed | Pkg Quantity | Price per package | Price per Unit | Price for qty needed | Link
 | Wii Nunchuk Controller | Ostent | Amazon | 1 | 1 | $11.49 | $11.49 | $11.49 | https://www.amazon.ca/dp/B00FJ2LMGK
 | Adafruit Wii Nunchuk Breakout | Adafruit | Digikey | 1 | 1 | $4.24 | $4.24 | $4.24 | https://www.digikey.ca/en/products/detail/adafruit-industries-llc/4836/13577615
 | Qwiic Cable - 50 mm | Sparkfun Electronics | Digikey | 1 | 1 | $1.37 | $1.37 | $1.37 | https://www.digikey.ca/en/products/detail/sparkfun-electronics/PRT-14426/7652739
 | Adafruit QT PY - SAMD21 | Adafruit | Digikey | 1 | 1 | 10.79 | $10.79 | $10.79 | https://www.digikey.ca/en/products/detail/adafruit-industries-llc/4600/13543375
 | USB C Cable | Cvilux USA | Digikey | 1 | 1 | $3.25 | $3.25 | $3.25 | https://www.digikey.ca/en/products/detail/cvilux-usa/DH-20M50053/13177348
 | Light Pipe 0.250" | Dialight | Digikey | 1 | 1 | $1.66 | $1.66 | $1.66 | https://www.digikey.ca/en/products/detail/dialight/51513030250F/4965201
 | Shipping |  | Digikey | 1 | 1 | $8.00 | $8.00 | $8.00
3D Printed Parts ESTIMATED PRICING USING 1KG ROLL COST: | $25.00
Part | Description |  |  | Quantity Needed | TOTAL Mass (g) | Estimated Price | Print Time (hr:Min) | Link
Top |  |  |  | 1 | 6 | $0.15 | 0:36
Bottom |  |  |  | 1 | 13 | $0.33 | 1:21
USB-C Cover |  |  |  | 1 | 1 | $0.03 | 0:01
 |  |  |  |  |  | $-
 |  |  |  |  |  | $-
 |  |  |  |  | Total Print Cost: | $0.50
Tools for Assembly
Alternatives (if there are other sources for some parts link them below)
Part and description | Link
 | Wii Nunchuk Controller | Adafruit | Adafruit |  |  |  |  |  | https://www.adafruit.com/product/342
 | Adafruit Wii Nunchuk Breakout | Adafruit | Adafruit |  |  |  |  |  | https://www.adafruit.com/product/4836
 | Qwiic Cable - 50 mm | Adafruit | Adafruit |  |  |  |  |  | https://www.adafruit.com/product/4399
 | Adafruit QT PY - SAMD21 | Adafruit | Adafruit |  |  |  |  |  | https://www.adafruit.com/product/4600

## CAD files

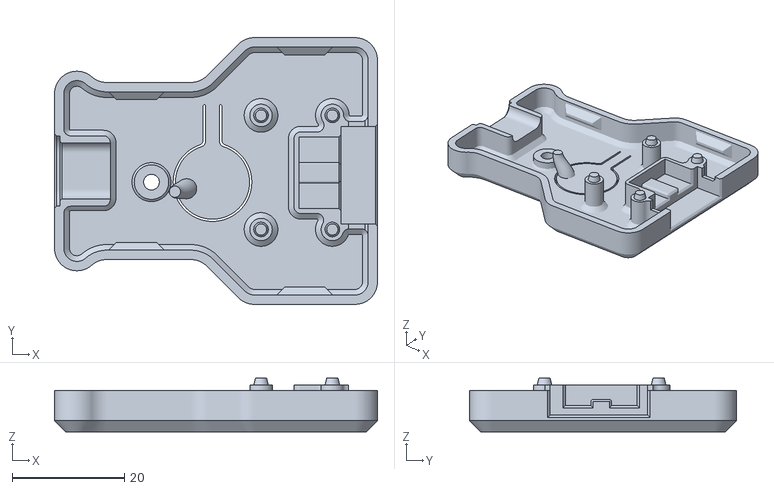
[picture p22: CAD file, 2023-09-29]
Build_Files/3D_Printing_Files/Ivy_Enclosure_Top.stl
57.5 x 47.5 x 9.60

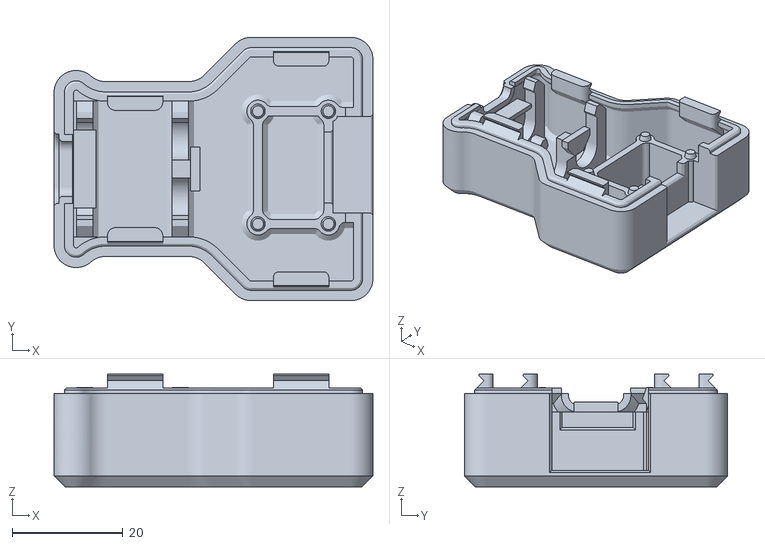
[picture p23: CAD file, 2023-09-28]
Build_Files/3D_Printing_Files/Ivy_Enclosure_Bottom.stl
57.5 x 47.5 x 20.3

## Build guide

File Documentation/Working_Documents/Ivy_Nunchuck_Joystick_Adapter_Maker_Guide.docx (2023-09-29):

# Overview

This document contains the necessary information to build the device.

This list provides an overview of the steps required to build and deliver the device.

Maker To Do List

- Read through the Maker Guide to become familiar with required components, tools, supplies, and safety gear and overall assembly steps.
- Talk to User about customization options (e.g., colour, any special requests, etc.)
- Order hardware components
- Print or obtain the 3D Printed Components
- Gather tools, supplies, and safety equipment.
- Assemble the device.
- Test device.
- Print “User Guide”.

Items to Give to User

- Assembled, tested device.
- “User Guide”.

# Tool List

A Computer with Arduino IDE for programming microcontroller.

# Customization Guide

## Enclosure Colour

The enclosure can be printed in the user’s desired colour.

## Multi-Color Enclosure

The enclosures can be printed in two colors with a filament swap at layer 5 / 1.00 mm to increase the contrast / visibility of the labels on the top (and bottom).

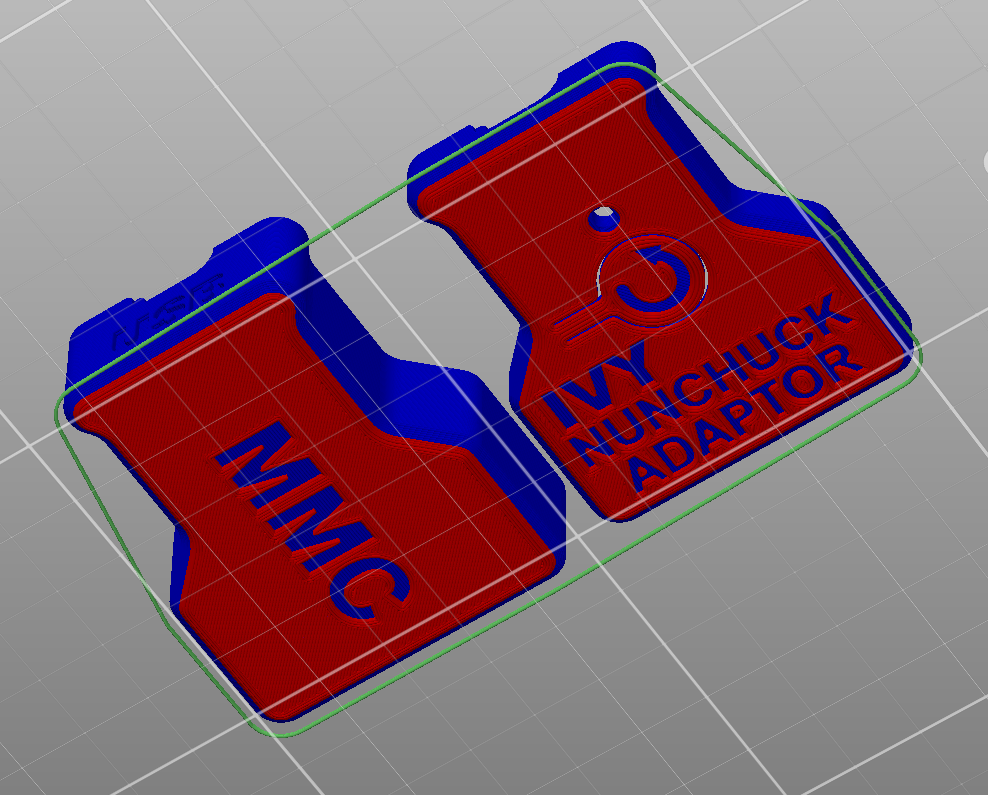
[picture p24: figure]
Screenshot showing a filament color swap at layer 5.

# 3D Printing Guide

## 3D Printing Summary

Metrics | Single Unit
Total Print Time (min) | 2h06m
Total Number of Components | 2
Typical Total Mass (g) | 22
Typical Number of Print Setups | 1

## 3D Printing Settings

Print File Name | Qty | Total Print Time (hr:min) | Mass (g) | Infill (%) | Support(Y/N) | Layer Height/ Nozzle Diameter(mm) | Notes
Ivy_Enclosure_Top.stl | 1 | 0:45 | 8 | 20 | N | 0.2/0.4
Ivy_Enclosure_Bottom.stl | 1 | 1:20 | 15 | 20 | N | 0.2/0.4

## Post-Processing

- Make sure the button is free to move
- Remove any stringing or blobs.

## Quality Prints

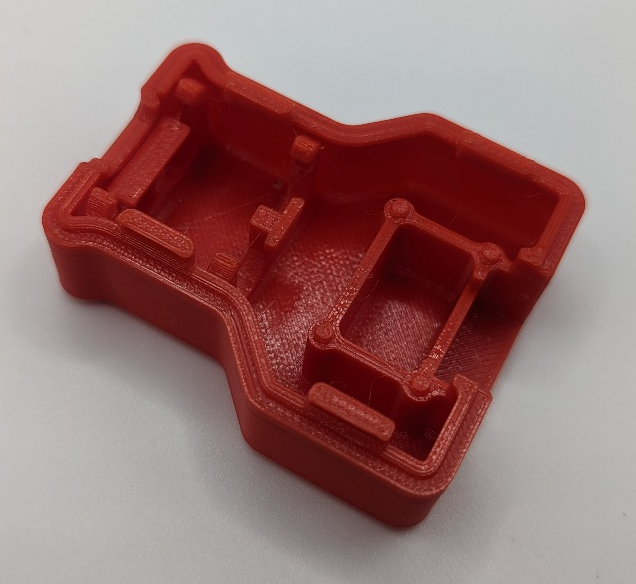
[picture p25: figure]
Inside of good quality Ivy Enclosure Bottom 3D print
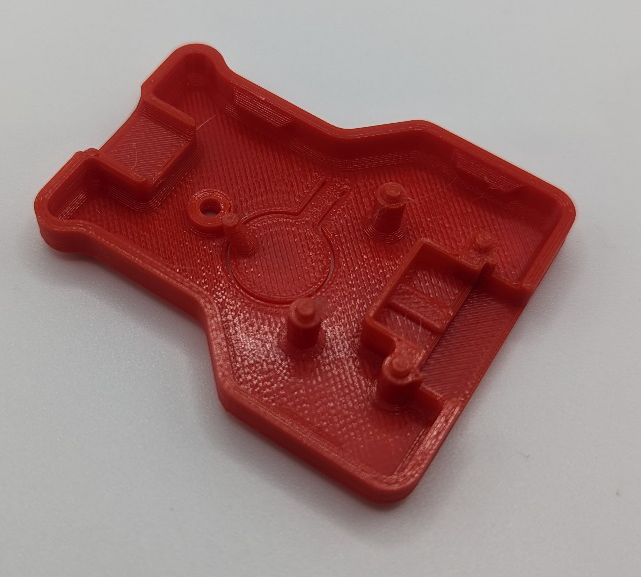
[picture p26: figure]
Inside of good quality Ivy Enclosure Top 3D print
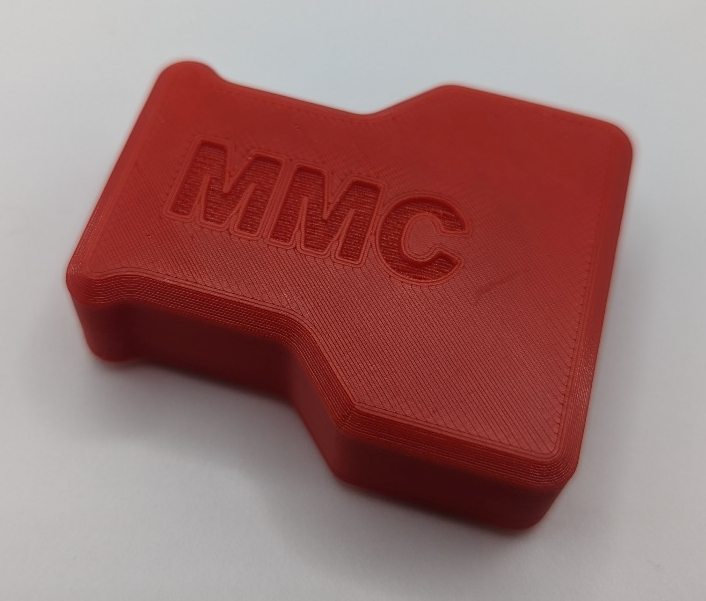
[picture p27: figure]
Bottom of good quality Ivy Enclosure Bottom 3D print
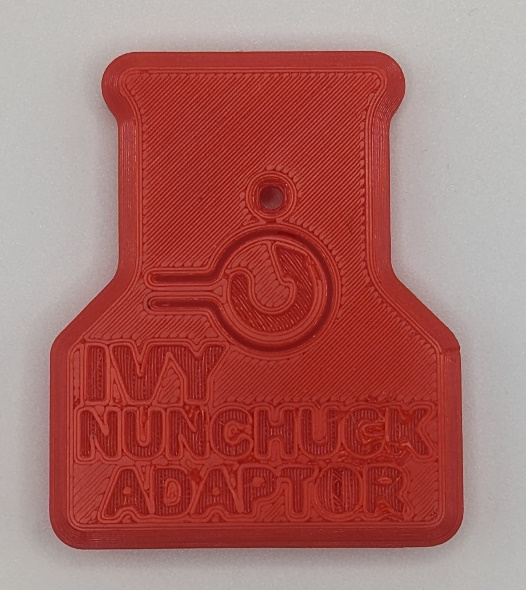
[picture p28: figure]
Top of good quality Ivy Enclosure Top 3D print

# Assembly Guide

The assembly of the Ivy Nunchuck Joystick Adapter consists of two steps: the assembly of the electronics into the 3D printed enclosure and flashing the firmware to the microcontroller.

## Part A: Enclosure Assembly

### Required Components

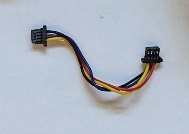
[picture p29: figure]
STEMMA QT Cable

1 | Adafruit QT Py SAMD21 Dev Board (https://www.digikey.ca/en/products/detail/adafruit-industries-llc/4600/13543375) | QTY 1 | 2 | | Adafruit Wii Nunchuck Breakout (https://www.digikey.ca/en/products/detail/adafruit-industries-llc/4836/13577615) | QTY 1 | 3 | Qwiic Cable - 50 mm (https://www.digikey.ca/en/products/detail/sparkfun-electronics/PRT-14426/7652739) | QTY 1

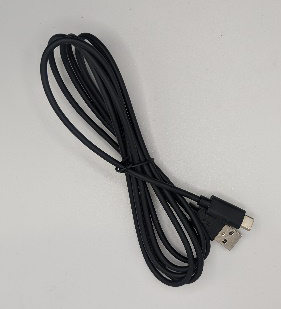
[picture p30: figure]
USB-C Cable
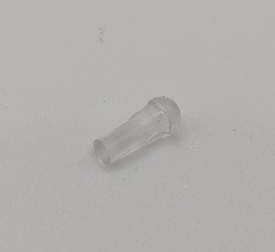
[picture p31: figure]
Light Pipe
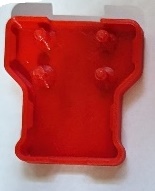
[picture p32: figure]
Enclosure Top

4 | 6 ft USB C – USB A Cable (https://www.digikey.ca/en/products/detail/cvilux-usa/DH-20M50053/13177348) | QTY 1 | 5 | | Light Pipe (https://www.digikey.ca/en/products/detail/dialight/51513030250F/4965201) | QTY 1 | 6 | Ivy Enclosure Top | QTY 1

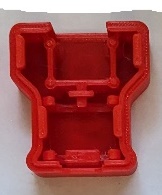
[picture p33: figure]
Enclosure Bottom
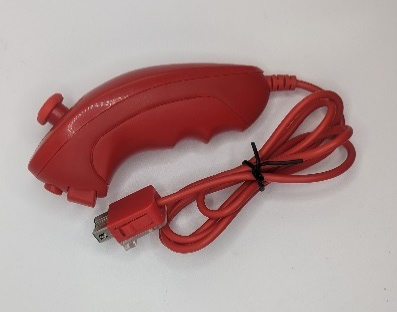
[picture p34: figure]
Nunchuck Controller

7 | Ivy Enclosure Bottom | QTY 1 | 8 | | Nunchuck Controller (https://www.amazon.ca/dp/B00FJ2LMGK) | QTY 1

### Required Tools

- None required.

### Required Personal Protective Equipment (PPE)

- None required.

### Part A Assembly Steps

#### Step A1: Attach STEMMA QT Cable to Microcontroller

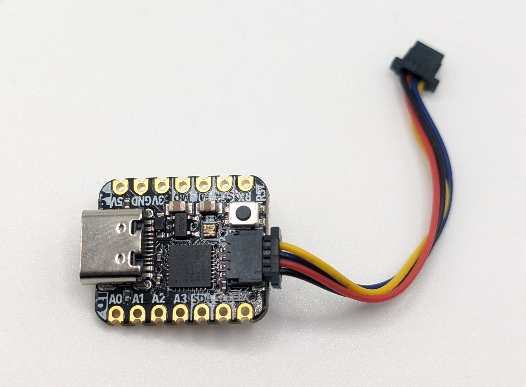
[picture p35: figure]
An Adafruit QT PY development board with a STEMMA QT cable attached.

Attach one end of the STEMMA QT Cable to the STEMMA QT connector on the Adafruit QT Py microcontroller.

#### Step A2: Attach STEMMA QT Cable to Nunchuck Breakout Board

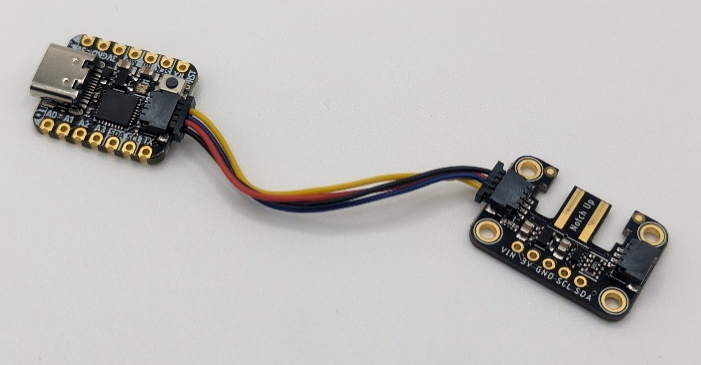
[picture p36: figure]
The Adafruit QT PY Development board and the Adafruit Nunchuck Breakout board attached by a STEMMA QT cable.

Attach the other end of the STEMMA QT Cable to one of the STEMMA QT connectors on the Nunchuck Breakout board.

#### Step A3: Insert QT Py into Bottom Enclosure

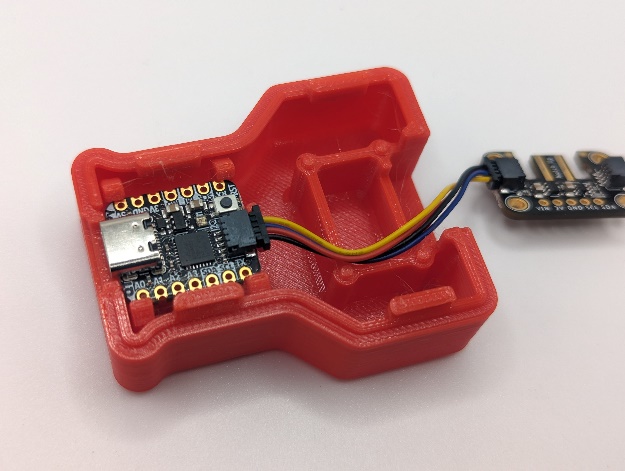
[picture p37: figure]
The Enclosure Bottom with the QT PY board inserted.

Align the QT Py USB connector into the corresponding opening in the Enclosure Bottom. Gently press on the board to lock it into place.

#### Step A4: Insert Nunchuck Breakout Board into Bottom Enclosure

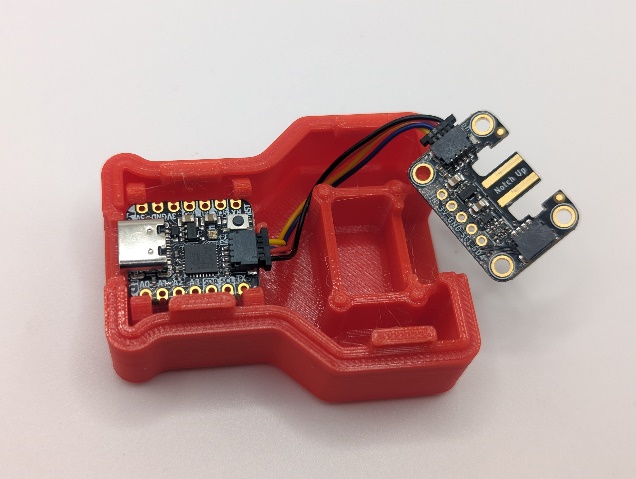
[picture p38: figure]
The Enclosure Bottom with the QT Py inserted, and the STEMMA QT cable tucked beside the posts.
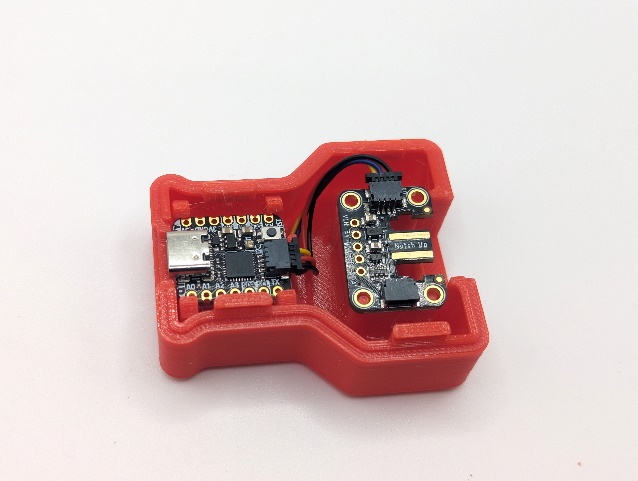
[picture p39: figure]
The Enclosure Bottom with both the QT Py and Nunchuck Breakout board inserted.

Position the Nunchuck Breakout Board so the mounting holes align with the posts. Tuck the STEMMA QT Cable down into the Enclosure Bottom.

#### Step A5: Connect Top Enclosure to Bottom Enclosure

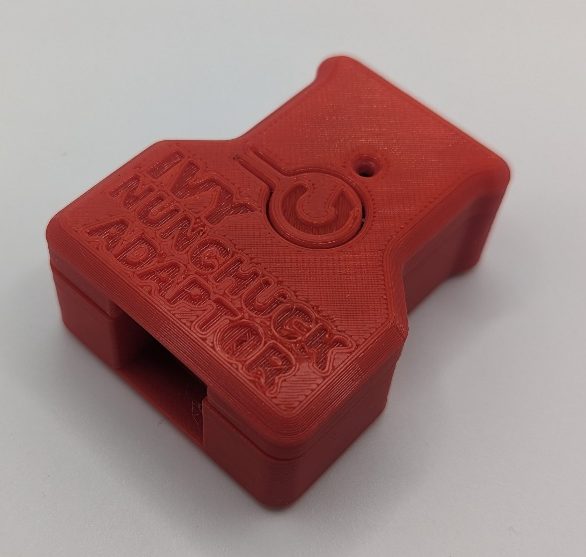
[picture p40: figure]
Assembled Ivy Nunchuck enclosure

Position the Top Enclosure over top of the Bottom Enclosure and press down to engage the snap fit.

#### Step A6: Insert the Light Pipe

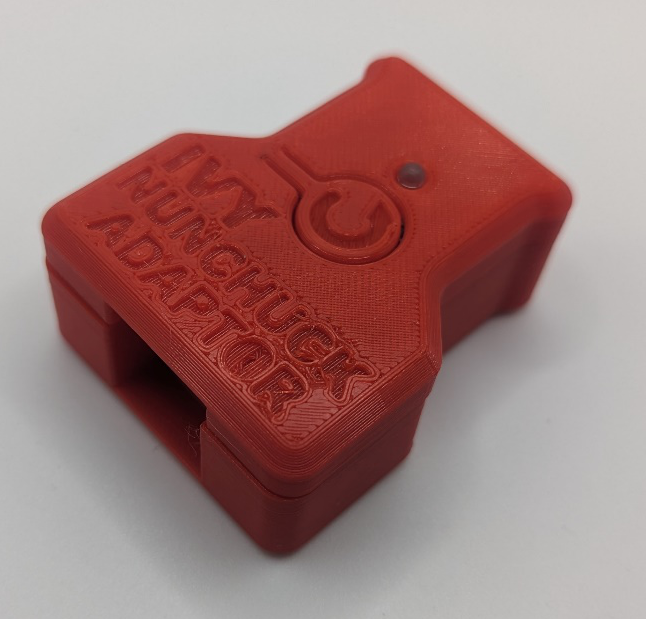
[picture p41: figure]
Assembled Ivy Nunchuck with Light Pipe inserted into top.

Insert the Light Pipe into the hole in the Enclosure Top.

#### Step A7: Plug in USB Cable and Nunchuck

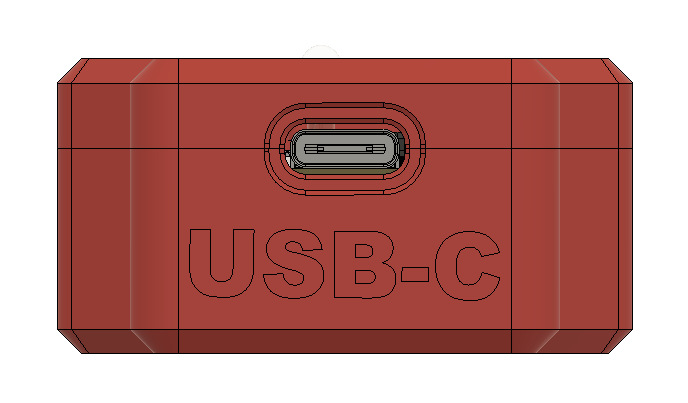
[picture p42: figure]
The USB connector side of the Ivy enclosure is labelled USB-C.

Plug in the USB C Cable on the side of the Enclosure labelled “USB-C”.

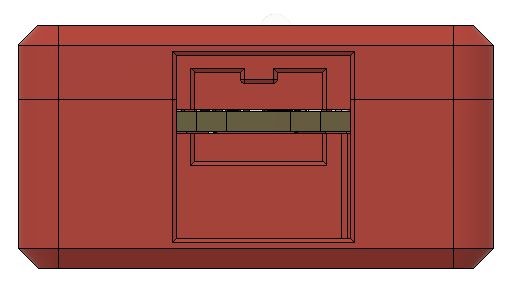
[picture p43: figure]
Nunchuck controller connection side of the enclosure with a rectangular-shaped opening.

Plug the Nunchuck controller on the opposite side of the Enclosure. The notch on the connector must be oriented towards the top.

#### Step A8: Admire your Assembled Ivy Nunchuck Joystick Adapter

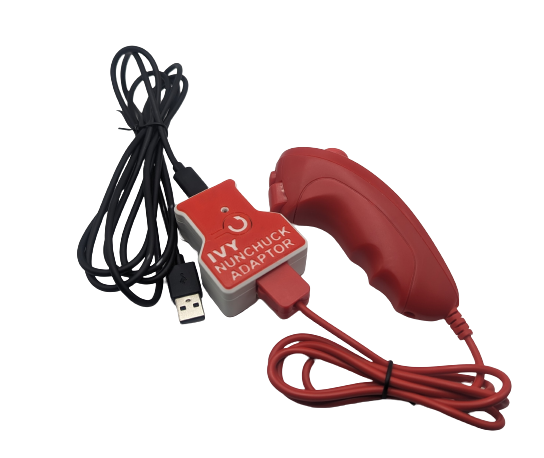
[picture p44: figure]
Ivy Nunchuck Adaptor with USB cable and Red Nunchuck controller attached.

The assembly is now complete.

## Part B: Firmware Installation

### Required Tools

- Computer with Arduino IDE to program microcontroller.

### Required Personal Protective Equipment (PPE)

- None required.

### Part B: Firmware Steps

#### Step B1: Setup Arduino IDE

1. Download Arduino IDE for your operating system at https://www.arduino.cc/en/software
2. Install the Arduino IDE.

#### Step B2: Setup Arduino IDE for QT Py Board

1. Open Arduino IDE.
2. Click on File -> Preferences.
3. Locate the text field that says Additional Boards Manager URLs beside it.
4. Copy and paste the following link into the field as a new line: https://adafruit.github.io/arduino-board-index/package_adafruit_index.json
5. Click on OK.
6. Restart the Arduino IDE.
7. Open the Boards Manager option from the Tools-> Board-> Boards Manager...,
8. Search for “Adafruit SAMD” and select “Adafruit SAMD Boards” by Adafruit.
9. Click Install to install the board.

#### Step B3: Install Libraries

1. In a web browser, go to https://github.com/cyborg5/TinyUSB_Mouse_and_Keyboard and go to Code -> Download ZIP.
2. In Arduino IDE, click Sketch -> Include Library -> Add .ZIP Library.
3. Navigate to the ZIP file downloaded in Step (a). Click OK.
4. Go to Tools -> Manage Libraries…, search for “Flash Storage” and install the library “FlashStorage” by Various.
5. Go to Tools -> Manage Libraries…, search for “Adafruit_Neopixel” and install the library “Adafruit_Neopixel” by Adafruit.
6. Go to Tools -> Manage Libraries…, search for “WiiChuck” and install the library “WiiChuck” by Kevin Harrington.

#### Step B4: Setup Local Code Directory

1. Download the Firmware_Files from the GitHub Repository: https://github.com/makersmakingchange/Ivy-Nunchuk-Joystick-Adapter/blob/main/Build_Files/Firmware_Files/Ivy_Joystick_Mouse_Firmware.zip
2. Extract / unzip the folder to a known location.
3. Confirm that you have the following folder structure:
- Ivy_Joystick_Mouse_Firmware (folder)
  - Ivy_Joystick_Mouse_Firmware.ino
  - OpenAT_Joystick_Response.h
  - XACGamepad.h

#### Step B5: Upload the Code to the microcontroller.

1. Open OpenAT_Ivy_Joystick_Mouse.ino with Arduino IDE.
2. Select Adafruit QT Py M0 (SAMD21) from Tools -> Board -> Adafruit SAMD Boards
3. Click on Tools -> USB Stack and select TinyUSB
4. Connect the Adapter using the USB cable to the computer.
5. Select the correct port from Tools -> Port menu.
6. Verify and upload the code.

# Testing

To test the Ivy Nunchuck Joystick Adapter, you will need the device itself and a host device. The host device can be a computer or an Android or Apple smartphone or tablet. Note that the Android and Apple options will require an USB OTG adapter cable to connect.

## Mouse

1. Plug the USB cable into a USB port on the Host Device.
2. Confirm that the Adapter is in Mouse Mode (Yellow Status Light). If not switch modes (see below).
3. Confirm that the mouse cursor moves when the thumbstick is moved.
4. Confirm that the buttons produce a left and right click when pressed.

## Gamepad

1. Plug the USB cable into a USB port on the Host Device.
2. Confirm that the Adapter is in Gamepad Mode (Blue Status Light). If not switch modes (see below).
3. If using Windows, open “Set up USB Game Controllers” from the Control Panel. You can find this by searching your computer in the search bar next to the Windows icon.
  a. Otherwise use https://hardwaretester.com/gamepad to test.
4. Ensure that the joystick is registered as a game controller and select your joystick from the list and go to “Properties”.
5. Move your joystick and observe the movement of the cross hatch in the “Axes” window. Ensure it moves in the proper directions when you move the joystick (the arrow points in the up direction). If not, open the joystick and check your connections.
6. Activate each button. Ensure that buttons 1 and 2 light up when you press the button and stops when you release the button.

## Switching Modes

1. Reset the Adapter by pressing the Reset Button or removing and replacing the USB Cable.
2. When the Status Light turns red, press and hold both the C Button and the Z Button on the Nunchuck.
3. When the Status Light turns green, release the buttons.
4. Press the C button (round button) to toggle between modes. The light on the Adapter will indicate the current mode: USB HID Mouse - Yellow, USB HID Gamepad - Blue.
5. Press and release the Z button (square button) to set the mode. The light will blink in the selected mode colour.
6. Reset the Adapter by pressing the Reset Button or removing and replacing the USB Cable.

© 2023 by Neil Squire Society. This work is licensed under the CC BY SA 4.0 License: http://creativecommons.org/licenses/by-sa/4.0 Files available at https://github.com/makersmakingchange/Ivy-Nunchuk-Joystick-Adapter Page 1 of 1

V1.0 | SEPTEMBER 2023 Ivy Nunchuck Joystick Adapter maker Guide

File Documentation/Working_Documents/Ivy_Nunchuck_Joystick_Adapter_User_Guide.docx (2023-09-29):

# Introduction

The Ivy Nunchuck Joystick Adapter enables a Nunchuck controller to be used as a USB HID Mouse or USB HID Gamepad. The Nunchuck Controller has a thumb joystick and two buttons. A status light on the enclosure of the Adapter indicates which operating mode the device is in.

# Features

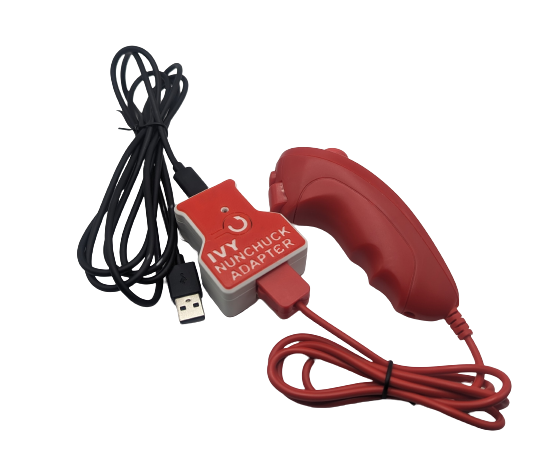
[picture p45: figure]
The Ivy Nunchuck Joystick Adaptor and its features.
The Ivy Nunchuck Joystick Adaptor and its features.

Status Light

Nunchuck Controller

USB-C Cable

Ivy Nunchuck Joystick Adapter

Nunchuck Thumbstick

Nunchuck
Z-Button

Nunchuck
C-Button

Reset Button

# Setup

1. Plug the Nunchuck Controller into the Ivy Nunchuck Joystick Adapter.
2. Plug the USB-C end of the USB Cable into the Ivy Nunchuck Joystick Adapter.
3. Connect the other end of the USB cable to the Host Device (use a suitable Adapter if necessary).
4. If desired, you can use hook and loop fastener to mount the Ivy Adapter.

## Swapping between Mouse and Gamepad Mode

1. Reset the Adapter. Before the red light turns off, press and hold the two buttons on the Nunchuck until the light turns green, then release the two buttons.
2. Press the C button (round button) to toggle between modes. The light on the Adapter will indicate the current mode: USB HID Mouse - Yellow, USB HID Gamepad - Blue.
3. Press and release the Z button (square button) to set the mode. The light will blink in the selected colour.
4. Cycle the power by pressing the reset button or disconnecting and reconnecting USB cable.

# Usage

Mouse Mode | Gamepad Mode
Status Light: Yellow | Status Light: Blue
- Move the joystick to control the cursor. - Press the C button to left click. - Press the Z button to right click. - Hold the Z button for 2 seconds to enter scroll mode. LED will turn purple. Move joystick to scroll. Press Z button again to exit scroll mode. | - Move the joystick to control the joystick. - Press the C button to activate Button 1. - Press the Z button to activate Button 2.

## Mapping

Nunchuck | Mouse | Joystick
| | PC | XAC (Left USB) | XAC (Right USB)
Joystick | Cursor movement (Scroll movement if in scroll mode (purple LED)) | Joystick movement | Left Thumbstick | Right Thumbstick
C (Round) | Left click | Button 1 | X1 (Left Stick Up) | View
Z (Square) | Right click (Long press -> enter scroll mode) | Button 2 | X2 (Left Stick Down) | Menu

Note: Default XAC mappings can be modified through the Xbox Accessories App. (https://support.xbox.com/en-CA/help/account-profile/accessibility/customize-adaptive-controller-in-xbox-accessories-app)

# Host Device Compatibility

- USB HID Mouse: PC, Mac, Android Smartphone, Apple Smartphone (iOS 13+)
- USB HID Gamepad: PC, Xbox Adaptive Controller, Android Smartphone, Apple Smartphone (iOS 13+)

# Specifications

Nunchuck Joystick Range of Motion | ±30°
Nunchuck Joystick Range of Motion | ± 15 mm
Nunchuck Joystick Activation Force | 100 grams
Nunchuck Weight | 68 grams
Enclosure Height | 25 mm
Enclosure Width | 48 mm
Enclosure Length | 58 mm
Enclosure Weight | 21 grams

# Cleaning

The outside of the enclosure can be cleaned with a damp cloth. Do not use hot water. Do not submerge.

© 2023 by Neil Squire Society. This work is licensed under the CC BY SA 4.0 License: http://creativecommons.org/licenses/by-sa/4.0 Files available at https://github.com/makersmakingchange/Ivy-Nunchuk-Joystick-Adapter Page 2 of 3

V1.0 | SEPTEMBER 2023 Ivy Nunchuck Joystick Adapter user Guide

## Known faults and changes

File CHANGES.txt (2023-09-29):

Version 1.0 | 2023-Sep-29
 - Extended enclosure to allow more cable clearance
 - reoriented, expanded label on top
 - 

Version 0.1.2 | 2023-Jul-24
 - Implemented scroll in code
 - Fixed software mode switching
 - Updated documentation

Version 0.1.1 | 2023-Jul-13
 - Modified top and bottom enclosure for better fit and function

Version 0.1 | 2023-Jun-30 
 - Ivy Nunchuck Adapter Minimum viable product
 - 3D Printed Enclosure
 - Solder-free STEMMA QT electronics assembly
 - Basic USB HID Mouse and USB HID Gamepad output

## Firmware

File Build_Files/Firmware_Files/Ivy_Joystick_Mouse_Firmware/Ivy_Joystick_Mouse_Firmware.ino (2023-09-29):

/*
  File: OpenAT_Ivy_Joystick_Mouse.ino
  Software: USB gamepad and mouse funtionality for a Nunchuck Controller.
  Developed by: Makers Making Change
  Version: (27 September 2023)
  License: GPL v3

  Copyright (C) 2023 Neil Squire Society
  This program is free software: you can redistribute it and/or modify it under the terms of
  the GNU General Public License as published by the Free Software Foundation,
  either version 3 of the License, or (at your option) any later version.
  This program is distributed in the hope that it will be useful, but WITHOUT ANY WARRANTY;
  without even the implied warranty of MERCHANTABILITY or FITNESS FOR A PARTICULAR PURPOSE.
  See the GNU General Public License for more details.
  You should have received a copy of the GNU General Public License along with this program.
  If not, see <http://www.gnu.org/licenses/>
*/
// This firmware enables a Nunchuck controller to be used as a USB HID Mouse and/or USB HID Gamepad. The Nunchuck Controller is connected
// via an Adafruit Wii Nunchuck Breakout Board through I2C to an Adafruit SAMD21 Qt Py development board.

#include "XACGamepad.h" // Definition of USB HID Gamepad compatible with Xbox Adaptive Controller
#include "OpenAT_Joystick_Response.h" // Non-linear mouse cursor speed response
#include <FlashStorage.h> // Non-volatile memory for storing settings
#include <TinyUSB_Mouse_and_Keyboard.h> // Convenience library for TinyUSB HID Mouse.
#include <WiiChuck.h> //Nunchuck communication
#include <Adafruit_NeoPixel.h> //Lights on QtPy


#define MODE_MOUSE 1
#define MODE_GAMEPAD 0

#define USB_DEBUG  0 // Set this to 0 for best performance.

#define UPDATE_INTERVAL   5 // TBD Update interval for perfoming HID actions (in milliseconds)
#define DEFAULT_DEBOUNCING_TIME 5

#define JOYSTICK_DEFAULT_DEADZONE_LEVEL      0              //Joystick deadzone
#define JOYSTICK_MIN_DEADZONE_LEVEL          0
#define JOYSTICK_MAX_DEADZONE_LEVEL          10
#define JOYSTICK_MAX_DEADZONE_VALUE          64             //Out of 127

#define JOYSTICK_MAX_VALUE                   127

#define JOYSTICK_NUNCHUCK_X_MIN 0
#define JOYSTICK_NUNCHUCK_X_MAX 255
#define JOYSTICK_NUNCHUCK_Y_MIN 0
#define JOYSTICK_NUNCHUCK_Y_MAX 255

#define SLOW_SCROLL_DELAY                    200            //Minimum time, in ms, between each slow scroll action (number of slow scroll actions defined below)
#define FAST_SCROLL_DELAY                    60             //Minimum time, in ms, between each fast scroll action (higher delay = slower scroll speed)
#define SLOW_SCROLL_NUM                      10             //Number of times to scroll at the slow scroll rate

#define LONG_PRESS_MILLIS                    2000

//#define JOYSTICK_REACTION_TIME             30             //Minimum time between each action in ms
#define SWITCH_REACTION_TIME                 100            //Minimum time between each switch action in ms
#define STARTUP_DELAY_TIME                   5000           //Time to wait on startup
#define FLASH_DELAY_TIME                     5              //Time to wait after reading/writing flash memory

#define MOUSE_MAX_XY                         6            // Mouse pixels per update at max deflection (max "speed")

//Define model number and version number
#define JOYSTICK_MODEL                        1
#define JOYSTICK_VERSION                      2


void resetJoystick(void); //forward declaration of reset function

XACGamepad gamepad;         //Starts an instance of the USB gamepad object
Accessory nunchuck;         //instance of nunchuck controller from WiiChuck library

// Declare variables for settings. Default values are written to flash memory on first run, then read back on
// subsequent power cycles.
int isConfigured = 0;
int modelNumber = 3;  // 1 - Forest Hub, 2 - Ivy Nunchuck Adapter, Enabled Controller Mini, 3 - 
int versionNumber = 1;
int deadzoneLevel = 1;
int operatingMode = MODE_MOUSE;   // 1 = Mouse mode, 0 = Joystick Mode


// Declarge variables to store in flash
FlashStorage(isConfiguredFlash, int);
FlashStorage(modelNumberFlash, int);
FlashStorage(versionNumberFlash, int);
FlashStorage(deadzoneLevelFlash, int);
FlashStorage(operatingModeFlash, int);

long lastInteractionUpdate;
long ZPressStartMillis = 0;

// Declare joystick input variables
int inputX;
int inputY;
int outputX;
int outputY;
int responseX = 0;
int responseY = 0;

//Declare switch state variables for each switch
int switchAState;           // Mouse mode = left click
int switchBState;           // Mouse mode = middle click
int switchCState;           // Mouse mode = right click
int switchJoyState;         // Mouse mode = left click              // Switch in the joystick (press down)

// Previous status of switches
int switchAPrevState = HIGH;
int switchBPrevState = HIGH;
int switchCPrevState = HIGH;
int switchJoyPrevState = HIGH;


int currentDeadzoneValue;

bool settingsEnabled = false;

//***API FUNCTIONS***// - DO NOT CHANGE
typedef void (*FunctionPointer)(bool, bool, String);

//Type definition for API function pointer

typedef struct {                                  //Type definition for API function list
  String endpoint;                                //Unique two character end point
  String code;                                    //Unique one character command code
  String parameter;                               //Parameter that is passed to function
  FunctionPointer function;                       //API function pointer
} _functionList;

//Switch structure
typedef struct {
  uint8_t switchNumber;
  String switchButtonName;
  uint8_t switchButtonNumber;
} switchStruct;


// Declare individual API functions with command, parameter, and corresponding function
_functionList getModelNumberFunction =            {"MN", "0", "0", &getModelNumber};
_functionList getVersionNumberFunction =          {"VN", "0", "0", &getVersionNumber};
_functionList getJoystickDeadZoneFunction =       {"DZ", "0", "0", &getJoystickDeadZone};
_functionList setJoystickDeadZoneFunction =       {"DZ", "1", "",  &setJoystickDeadZone};

// Declare array of API functions
_functionList apiFunction[5] = {
  getModelNumberFunction,
  getVersionNumberFunction,
  getJoystickDeadZoneFunction,
  setJoystickDeadZoneFunction
};

//Switch properties
const switchStruct switchProperty[] {
  {1, "A", 1},
  {2, "B", 2},
  {3, "C", 3},
  {4, "Joy", 4}
};

Adafruit_NeoPixel pixels(1, PIN_NEOPIXEL);  // Create a pixel strand with 1 pixel on QtPy

//***MICROCONTROLLER AND PERIPHERAL CONFIGURATION***//
// Function   : setup
//
// Description: This function handles the initialization of variables, pins, methods, libraries. This function only runs once at powerup or reset.
//
// Parameters :  void
//
// Return     : void
//*********************************//
void setup() {
  pixels.begin(); // Initiate pixel on microcontroller
  pixels.setPixelColor(0, pixels.Color(255, 0, 0)); // Turn LED red to start
  pixels.show();

  if (USB_DEBUG) {
    Serial.begin(115200);
  } else {
    //Serial.end();
  } // endif

  // Read Memory
  readMemory();
  delay(FLASH_DELAY_TIME);

 // Begin HID gamepad or mouse, depending on mode selection
  switch (operatingMode) {
    case MODE_MOUSE:
      Mouse.begin();
      break;
    case MODE_GAMEPAD:
      gamepad.begin();
      break;
    default:
      break;
  }

  // Initialize Joystick
  initJoystick();
  
  if (USB_DEBUG) {
    while (!Serial) {
      delay(1);
    }
    Serial.println("USB Debug mode on. Change flag in code for best performance.");
  }
  
  checkSetupMode(); // Check to see if operating mode change

  delay(STARTUP_DELAY_TIME); //startup delay to faciliate reprogramming

  // Turn on indicator light, depending on mode selection
  switch(operatingMode) {
    case MODE_MOUSE:
      pixels.setPixelColor(0, pixels.Color(255, 255, 0)); // Turn LED yellow
      pixels.show();
      break;
    case MODE_GAMEPAD:
      pixels.setPixelColor(0, pixels.Color(0, 0, 255)); // Turn LED blue
      pixels.show();
      break;
  }

  lastInteractionUpdate = millis();  // get first timestamp

}

void loop() {

  settingsEnabled = serialSettings(settingsEnabled); //Check to see if setting option is enabled

  if ((millis()-lastInteractionUpdate) >= UPDATE_INTERVAL) {
    lastInteractionUpdate = millis();  // get timestamp
    readJoystick();
    readSwitch();

    joystickActions();

    switch(operatingMode){
      case MODE_MOUSE:      // Perform Mouse HID buttons
        mouseSwitches();
        break;
      case MODE_GAMEPAD:    // Update Gamepad HID buttons
        joystickSwitches();
    }
  }
  delay(1);
}

//*********************************//
// Joystick Functions
//*********************************//

//***READ Memory FUNCTION***//
// Function   : readMemory
//
// Description: This function reads values from Memory. The first time it is called, it writes default values.
//
// Parameters : void
//
// Return     : void
//****************************************//
void readMemory() {
  //Check if it's first time running the code
  isConfigured = isConfiguredFlash.read();
  delay(FLASH_DELAY_TIME);

  if (isConfigured == 0) { //Define default settings if it's first time running the code

    //Write default settings to flash storage
    modelNumberFlash.write(modelNumber);
    versionNumberFlash.write(versionNumber);
    deadzoneLevelFlash.write(deadzoneLevel);
    operatingModeFlash.write(operatingMode);

    //Mark as configured.
    isConfiguredFlash.write(1);
    delay(FLASH_DELAY_TIME);

  } else {
    //Load settings from flash storage
    modelNumber = modelNumberFlash.read();
    versionNumber = versionNumberFlash.read();
    deadzoneLevel = deadzoneLevelFlash.read();
    operatingMode = operatingModeFlash.read();
    delay(FLASH_DELAY_TIME);
  }

  //Serial print settings
  Serial.print("Model Number: ");
  Serial.println(modelNumber);

  Serial.print("Version Number: ");
  Serial.println(versionNumber);

  Serial.print("Operating Mode: ");
  Serial.println(operatingMode);

  Serial.print("Deadzone Level: ");
  Serial.println(deadzoneLevel);
}


//*********************************//
// Joystick Functions
//*********************************//

//***INITIALIZE JOYSTICK FUNCTION***//
// Function   : initJoystick
//
// Description: This function initializes joystick as input.
//
// Parameters : void
//
// Return     : void
//****************************************//
void initJoystick()
{
  getJoystickDeadZone(true, false); //Get joystick deadzone stored in memory
  nunchuck.begin();

  if (USB_DEBUG) {
    Serial.println("Deadzone set. Nunchuck initialized.");
  }
}

//***READ JOYSTICK FUNCTION**//
// Function   : readJoystick
//
// Description: This function reads the current raw values of potentiometers, checks if values exceed deadband, and calculates
//              joystick movements. Outputs true if joystick should be moved.
//
// Parameters :  Void
//
// Return     : Void
//*********************************//
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

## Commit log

2023-06-30 Update README.md
    Update links for device naming
2023-07-13 v0.1.1 Enclosure Updates
    -Remove USB C Cover
    -Add tighter knockout for USB C connector to top and bottom enclosure components
    -Fix reset button interference
    -Update documentation
    [Bottom.stl, Ivy-Nunchuck-Joystick-Adapter_BOM.xlsx, Ivy-Nunchuck-Joystick-Adapter_BOM_v0.1.1.csv, Ivy-Nunchuck-Joystick-Adapter_BOM_v0.1.1.xlsx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]
2023-08-23 V0.1.2
    Internal test build.
    [Ivy-Nunchuck-Joystick-Adapter_BOM.csv, Ivy-Nunchuck-Joystick-Adapter_BOM.xlsx, Ivy-Nunchuck-Joystick-Adapter_BOM_v0.1.1.csv, Ivy-Nunchuck-Joystick-Adapter_BOM_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]
2023-09-28 Naming and cleanup
    [Ivy-Nunchuck-Joystick-Adapter_BOM.csv, Ivy-Nunchuck-Joystick-Adapter_BOM.xlsx, Ivy_Nunchuk_Joystick_Adapter_Bottom.stl, Ivy_Nunchuk_Joystick_Adapter_Top.stl]
2023-09-28 v1.0 stls
    [Ivy_Enclosure_Bottom.stl, Ivy_Enclosure_Top.stl]
2023-09-29 v1.0 update
    [Ivy-Nunchuck-Joystick-Adapter_BOM.csv, Ivy-Nunchuck-Joystick-Adapter_BOM.xlsx, Ivy_Enclosure_Bottom.stl, Ivy_Enclosure_Top.stl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]
